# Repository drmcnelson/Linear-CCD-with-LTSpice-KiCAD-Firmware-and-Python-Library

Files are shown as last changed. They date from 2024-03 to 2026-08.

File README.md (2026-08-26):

# Linear-CCD-with-LTSpice-KiCAD-Firmware-and-Python-Library
by Dr M C Nelson (C) 20220-2026 [(the authoritative repo is here)](https://github.com/drmcnelson/Linear-CCD-with-LTSpice-KiCAD-Firmware-and-Python-Library)

<br>

> **Note:** For the **high-linearity version** for quantitative science along with a revised implementation of this all-in-one design but now with hardware locked timing (using the FlexPWM), please see the newer repository: [TCD1304-Sensor-Device-with-Linear-Response-and-16-Bit-Differential-ADC](https://github.com/drmcnelson/TCD1304-Sensor-Device-with-Linear-Response-and-16-Bit-Differential-ADC).

<br>

## Introduction
Linear CCDs can be useful tools in science, for example as a sensor for a spectrometer or imaging system.  And indeed, there are many commercial instruments that are based on low cost linear CCDs such as the Toshiba TC1304 and the Sony IXL511.
Here we provide design files, firmware and software for a device that provides competitive performance and a rich set of science-centric features, and that can be customized to your experiments, all at a fraction of the cost of the commercial offerings.  The design is based on the Toshiba TCD1304 (3648/3694 pixels) and Teensy 4.0 (600MHz ARM, 480MHz USB).  The Teensy 3.2 is plug compatible for this design.
Read further below, and you will find tutorials on electrical design and managing the CCD to provide flexible timing and reproducible measurements so that you can use it as a scientific instrument.

In this repository you will find directories containing (a) electrical design files in KiCad, (b) firmware (a sketch file) for the Teensy, and (c) a Python class library with graphical and command line utilities to operate the device.
The device has a trigger or gate input, sync and busy outputs, and spare pins for digital and analog I/O.
The operating modes include clocked, triggered frames, triggered series of frames, and gated frames (where the shutter is opened and closed on the rising and falling edges of the logic level input signal).
The device appears as a serial port (COM in windows) with comands and response in human language ASCII and frames returned as binary or formatted.
The python class library provides higher level functions, a graphical realtime display and a command line processor.  There is a help command in the firmware and in the Python command line interpreter.  Details of the electrical and firmware design are described later in this README.

The following shows the microcontroller side of the device.  The sensor side can be seen in the image of the spectrometer (below).   The digital I/O pins across the top include trigger input, sync and busy output, pins that monitor the signals going to the sensor, and spares that can be controlled through the user interface.  Across the bottom there are pins that can be used for analog inputs or digital I/O, and 3.3V that can be used for an auxiliary device.

IMG_20231215_144019112_cropped250

Following are two examples of applications; using the sensor in a spectrometer and measurement of spectral-spatial-dynamics in an OLED.  This repository provides what you need in terms of ecad files and software to build one for yourself, or if you like you can contact me for an assembled board.

The files in the repo were produced on a Linux desktop computer (Fedora 37, Cinnamon Spin), using KiCAD 6 for the electrical design and Emacs for the firmware and python programs.

<ul>
 <i>
For next level designs and a preview of our study on linearity and reproducibility in CCDs see our new repo at <a href=https://github.com/drmcnelson/TCD1304-Sensor-Device-with-Linear-Response-and-16-Bit-Differential-ADC>TCD1304 with linear response and 16bit ADC</a>. We suggest perusing both this and the new repo and selecting the implementation that best serves your needs.  Feel free to contact me with questions.
 </i>
</ul>

## Some Example Use Cases

### Spectrometer
The first shows the inside of a spectrometer built with a G1200 grating, two lenses and a slit. The mounts are 3D printed and everything is affixed to a stiff Al plate. There is a cover, not shown here, and specific surfaces are covered with low-reflectance tape.  The spectrum is that of a fluorescent ceiling light through a 200um fiber at a distance of about 8ft, with a 200um slit.

|IMG_20231217_120419719 cropped350|FluorescentLamp Screen500|

### Imaging Spectral-Spatial-Dynamics
The following example uses the sensor device to record the time evolution of the spatial distribution of light produced by an OLED at a current density of 150 $\mu A/cm^2$. The sensor device collects a series of frames wth 10ms shutters at 10ms intervals (back to back), with the series initated on a trigger at the start of the applied voltage waveform. The blue line shows the resulting current density in the OLED, the pale line shows the sync pulses output by the sensor device at the start of each frame, and the red line is the applied voltage (2.41V).  (We plan to post repositories for the DAQ board and current amplifier as well.)

|SampleR1 51 D7_G100K_A2 410v_I0 010s_D0 500s_N005_T4 0C_M17 0000mm_W501 340nm 20230309 080608 827395 tdaq2|SampleR1 51 D7_G100K_A2 410v_I0 010s_D0 500s_N005_T4 0C surface cropped|

# Electrical Design, Analog
The datasheet for the TCD1304 can be found here  https://toshiba.semicon-storage.com/us/semiconductor/product/linear-image-sensors/detail.TCD1304DG.html.
The following table is found on page 4.
We see that $V_{SAT}$ the saturation output volage runs from 450mV to 600mV, $V_{MDK}$ the dark signal is 2mV, thus a dynamic range of 300 (for a 10ms integration integral), $V_{OS}$ the DC output signal is typically 2.5V but can be from 1.5V to 3.5V, and $Z_O$ the output impedance is typically 500 ohms but can be 1K.  So, that is a lot of variation that we need to account for in our design.

TCD1304-optical-electrical

The datasheet provides the following diagram in Note 8 to illustrate the definition of $V_{OS}$.  The hatched area is the negative going output signal.  SS is ground

TCD1304-electrical-note8

For best performance in digitizing the signal, we want a circuit that takes the above signal as input and outputs a signal that matches the input range of our microcontroller's ADC.  The following circuit element shows one approach that does this and can run on a single supply. We can call this a shift, flip and amplify (SFA). The gain is set as usual for an inverting amplifier by $R_2$ and $R_1$ and the potentiometer provides the offset through the + input of the opamp.

SimpleSchematic1

But, recall that the datasheet says the output impedance $Z_0$ varies from 500 ohms to 1k.  If we connect that directly to our SFA then $Z_0$ becomes part of the gain equation, $R1\rightarrow R1+Z_0$, and in a bag of sensors we might find that the gain is different for each sensor.
So, we need to isolate that source impedance from the SFA.

A solution to this is to use an opamp follower as the first stage, as shown in the following crcuit.  The follower presents a very high impedance at its input, which is ideal for reading the voltage from the sensor, and a low impedance at its output, which is ideal as an input to the SFA

TCD1304-opampfollower

Referring again to the datasheet for the TCD1304, we see that (a) we can operate the sensor chip in the range 3V to 5.5V, (b) it requires a clock between 800KHz and 4MHz (2MHz if operated below 4V) and (c) the data readout rate is 1/4 of the clock 200kS/s to 1MS/s (500KS/S if powered below 4V).
Operating with a 3.3V supply, and making efficient use of the full scale range of the ADC,  means that we need to use a rail to rail opamp.
Our SFA architecture means that the opamp has to also have a wide common mode range. 
And the sampling rate means we need to look for a slew at least as faster as 100V/usec

The complete analog front end circuit is shown in the following LTSpice model based on the ADA4807.
We use the first opamp in the package for the voltage follower and the second opamp for the flip, shift,and amplify stage.
Gain and offset are as calculated above.
The green trace is the output from the sensor and the purple curve is the output from the second stage.
As can be seen the 2.5V to 1.9V signal from the sensor becomes a 0.1V to 3.1V for the ADC, and the rise time is small compared to the sampling period.
In our actual circuit we use a trim pot for the voltage applied to V+.

Screenshot from 2023-12-18 08-43-01

It might be noted that we could have chosen a larger gain to look at lower intensity light, or with the Teensy 3.2 we can use its built-in amplifier under software control, provided the offset is small.

## Analog input of the Teensy 4.x and Teensy 3.2
The following diagaram for the analog input, and one similar to this, are found in the datasheets for the i.MXRT106x (Teensy 4) and the K20 (Teensy 3).
This is a modified version of a SAR type analog input.  Normally the input sees the switched sampling capacitor.
Here there is a series resistor in front of the sampling capacitor.

T3analoginput

In operation, the switch closes for a period of time to allow the capacitor to draw charge from the input.
At the end of the sampling period the switch is opened and the voltage on the capacitor is converted to a digital representation in the successive approximation register (SAR).
In other words, precision is determined by the length of the sampling window (in time) versus the RC time constant seen by the sampling capacitor.
Full precision means the voltage on the capacitor is within 1 LSB of the input, at the end of the sampling window.

For a simple RC network, the voltage on the capacitor is $V(t)/V(0) = 1 - exp(-t/RC)$.
Therefore, for n bits of precision, the sampling window needs to be at least $ln(2^{n}) \times RC$.
This works out to be 11 x RC for 16 bits and 8 x RC for 12 bits. 
The following shows this graphically.

samplingtime

For the T3 in 16 bit mode, with RADIN = 2k, and CADIN = 8pf, RC ~ 16nsecs.
The voltage on the sampling capacitor is within $1/2^{16}$ of the input voltage after about 170nsecs.

For the T4 in 12 bit mode, RADIN can be from 5k to 25k and CADIN is 1.5pF, RC ~ 7.5nsecs to 40nsecs.
We need about 60nsecs to 320nsecs to reach 12 bit precision.

Thus the T3 and T4 are both compatible at 500KSPS.  See the [ADC library](https://github.com/pedvide/ADC) for details setting the sampling time and conversion clock.

The tradeoff for the T3 with its 16 bit input, is that the T3 has a much slower USB interface, 1MB/s transfers to the host versus 60MB/s for the T4.
The best frame to frame interval with the T3 is about 16msecs and about 8msecs for the T4.

N.B.  Driving the analog input of an MCU is different from driving a normal SAR type ADC.  Normally, the drive circuit for a SAR includes an external capacitor to serve as a charge reservoir for the sampling capacitor.  This is pre-empted in the MCU analog input by the large internal resistance in series with the sampling capacitor.

## How many bits do I really need?
In the table above, the dynamic range is listed as 300.
This is simply the saturation output voltage 600mv divided by the dark signal 2mV.
If that were the limit, then 10 good bits would be enough.

In principle the dark noise should scale with exposure time or by cooling.  Emperically, using a special low noise linear radiometric design(*), we find that the noise floor for the TCD1304 seems to be at about 0.6mV which it reaches for exposures below about 10msec.  Modest cooling to 4C is reported elsewhere to reduce noise by a factor of 4.  So, we can estimate a practical limit for the dynamic range at about 4,000, or 12 bits.  That is what is offered by the T4 ADC.  If you want to do signal averaging, and given the usual performance specs of ADCs, it is reasonable to have some extra bits, and so a 16 bit ADC is a good choice for a high performance system.

Our analog section uses an ADA4807.  Its datasheet lists the input voltage noise as $3.1 nV/\sqrt Hz$.
At 500KSPS this becomes 2.2uV, and setting the gain at 5, we expect 10uV.  So, we are well ahead of the noise floor for the device.
Without going into a more detailed analysis, we see that our electrical noise can be about 1/2 of the dark signal.
That is workable with some signal averaging.

(*) Our high performance designs with differential signal paths and ADC are posted at
[TCD1304 Sensor Device with Linear Response and 16 bit Differential ADC](https://github.com/drmcnelson/TCD1304-Sensor-Device-with-Linear-Response-and-16-Bit-Differential-ADC)
and
[S11639-01 with 16 bit differentual ADC for SPI](https://github.com/drmcnelson/S11639-01-Linear-CCD-PCB-and-Code).
 Both of these have been built and tested and the repos now have all of the gerbers, bom, firmware and user code.
We plan to upload a repo with a cooled sensor in the near future.   The other advantage of those designs is that they are two board systems and provide better mechanical isolation if your are changing cables after alignment.  But, the design posted here offers sufficient precision and has fewer parts (i.e., it costs less and takes less time to build).

# CCD operation
Operationally, a CCD sensor stores charge in each pixel proportional to light and noise, until assertion of a shift pin causes the contents to be transferred to a buffer and then the contents are shifted along the buffer by a clock to the output pin and appear as a series of voltages.
The TCD1304 has an additional function that controls which shift assertions initiate the readout sequence.
The internal structure is depicted as follows from page 3 of its datasheet.  Externally the device is controlled by three pins, shift SH, integration clear gate ICG, and master clock $\phi M$.

TCD1304-registers

The following two figures from the datasheet show how Toshiba envisions operation of the sensor chip.  As indicated, charge is integrated during the intervals between trailing edges at the SH pin. When the the ICG pin is low the accumulated charges are available in the readout buffer and then shifted to the output pin at a rate of 1 datum per four cycles of the master clock.

TCD1304-timing1

TCD1304-timing2

Toshiba labels the second diagram above as "Electronic Shutter Function".  This refers to the function of ICG in selecting which SH assertion results in charge being available in the readout buffer.  However it is not a shutter in the conventional sense.  It is easily shown experimentally that if the device is left idle, several SH cycles are needed to arrive at a noise level baseline in the readout.   There are a number of commerical CCD systems that clock the SH pin or its equivalent to keep the sensor "clean".  This can have important ramifications if the device is to be triggered, for example for kinetic studies.   Alternatives include good "dark" management, designing the experiment to start with a few blank frames to clear the sensor, and/or having the device initiate the trigger.

Note that it is the low state on the ICG pin that makes the readout available to be clocked out to the OS pin, while the SH pin sets the integration interval.

## Driving the SH, ICG and Master Clock pins
Referring again to the datasheet, page 6, we find the following table.
Notice that the shift gate has a capacitance of 600pF and the integration clear gate has 250pF.
From the magnitude of the capacitances, we might guess that these are closely related to moving charge to the output buffer.



Notice also, that the master clock and data transfer rates are reduced when operating at lower voltages.



The large capacitances also factor into how we drive these pins, rise times with large capacitances are easily current limited.
The preferred way to drive the gate pins is with a buffer and series resistor, as shown in the following.
For a 3.3V drive, a 150 ohm resistor sets the rise to 90nsecs for the SH pin and limits the current to 22mA.
For a 1 usec pulse, this gives a rise time that is less than 1/10 of the pulse width.
The buffer can be a 74LVC1G34, or one channel of a 74VLC3G34, which can drive 25mA.

singlegate

For comparison, the Teensy digital I/O pins provide 4mA.
If the gate is driven directly from the Teensy, the response is current limited, $\Delta t \approx C \Delta V / I$.
That works out to 500nsecs.
So, driving the gates from the digital I/O pins can work, if you can accomodate the longer pulse duration needed for the current limited pulse rise time.

In this repo we provide two sub-directories for designs for the all-in-one TCD1304 and Teensy, with and without the 25mA pulse driver (74VLC3G34).  The verion with 25mA gate drivers is the preferred version.  The KiCad files for that version are [here](TCD1304Rev2GDKiCAD).

For our high-end board with 16 bit ADC and faster timing, see our repo here.

## Frame rates, shutters and timing for data acquisition.
The following diagram from page 9 of the datasheet shows the timing requirements for the ICG and SH pins relative to each other and the master clock.

TCD1304-timingreqs

With a 2MHz master clock, it takes about 7.4ms to read one record from the device into the memory of the microcontroller.  Transfer from the microcontroller to the host PC can take an additional 5ms for the Teensy 3.x (12 Mb/s) or about 120usec with the Teensy 4.x (480 Mb/s).  Needless to say, this sets the maximum frame rate, that is the time between readouts, and is different from the minimum integration interval which depends only on the minimal interval between successive trailing edges at the SH pin.

For data collection, we need to be able to set integration and frame intervals freely (within the physical limits of the sensor) and we need to be able to reliably control timing with respect to an external trigger or gate.   Since the shutter or integration interval is defined by successive assertions of the SH pin, we focus on how these requirements translate to operation of this pin.

The following diagram shows a sequence where the shutter interval is shorter than the inter frame interval, and the frame interval is not necessarily an integer number of shutter intervals in length.  The SH pin operates with alternating short and long intervals.  The frame interval is the sum of these two intervals, or that betwen every second SH.

Shutter-Operation-shortshutter

The following shows back to back shutters with identical frame and shutter intervals.

Shutter-Operation-longshutter

And this one shows a constant shutter interval with the frame interval an integer multiple of the shutter.

Shutter-Operation-modalshutter

Our control logic for operating the device has to accomodate all three scenarios, and we have to be able to initiate frames or sets of frames from a clock or from a trigger.
Architecturally, we set this up as two ISRs, which we call ShutterA_isr() and ShutterB_isr().  The sequences are easily implemented by various combinations of A and B or just B after one A, and easily triggered, gated or clocked as needed.

## Signals, Sync and Busy
The sensor device has a trigger input and two outputs SYNC and BUSY.  Sync can be configured to signal the start of a series of frames or to signal the start of each shutter.  SYNC can also be configured to be followed by a holdoff.  BUSY is set with the start of the first shutter and remains asserted until the last data transfer is complete.   Each pin can be set nominally HIGH or LOW, assertion is the opposite.  Additionally there is a SPARE pin.  Any of the pins can be manually set, cleared, toggled or pulsed.

The following shows the actual operation of the sensor device, green is SH, purple is ICG, blue is SYNC and yellow is BUSY.  We see BUSY goes high immediately, SH and ICG operate as described in the data sheet.  Light is integrated between the two trailing edges and the data is transferred following the second assertion of the SH and clearing of the ICG pins.

Scope-singleframe

## Triggered and gated operation
The following shows a triggered frame.  The commands are "set trigger rising", "trigger 20" to trigger one 20usec frame.  The blue line is the trigger input.  There is a small reproducible delay between the trigger and the shutter, due to certain fixed timings involved in getting the shutter started.  Notice the alignment of the BUSY and SH signals.

Scope-triggerd

The following shows a gated frame, blue is the gate signal.  The commands are "set trigger change", "gate 1", to gate one frame.  For this, the spare pin is connected to the trigger input and we enter the command "pulse spare 20" to output a 20 usec pulse.  As you can see the shutter sequence begins and finishes with the gate.

Scope-gated

# Data processing
Referring to the clock diagrams above, we see that the data record comprises 12 dummy outputs followed by 13 light shielded elements, followed by 3 shadowed elements, followed by the 3648 elements making up the effective output and followed by another 14 dummy elements.   Thus elements 12 thru 24 provide a baseline which we can average or take the median and subtract from elements 28 through 2675 which form the image.   In the spirit of "always preserve primary data", we do not do this substraction nor any scaling, in firmware.  Rather we pass the entire record as is, to the PC host and the host software is responsible for subtracting and scaling as appropriate.

# Firwmare
The firmware subdirectory contains a sketch for Teensy 4.0.  After assembling your board (or obtaining one from the author), you can mount your Teensy 4 and TCD1304 detector, and then flash the program into the Teensy 4.0.   The commands are in english, ASCII over USB.  Enter the command "help" to get a listing and short explanation of the commands.  A listing of the help text is included in the Python subdirectory.

The default action returns the data in binary.  You will ideally want to use a multi-threaded program on your host computor, with one thead reading the responses and data and queuing as appropriate to a separate graphics thread.   The Python code provides a Class for the device that handles all of this.

# Python
The Python subdirectory contains a file TCD1304Rev2Controller.py and three library files that it looks for in its directory.  The program implements threads using the multitasking interface in Linux.  A dedicated thread reads the responses from the device and queues data to an internal data queue for the "save" command and to a queue read by the runtime graphics thread.  The Python program has a help command, like the firmware.

# Adjusting the offset
With a voltmeter or scope, the middle pin on the trim pot should be set close to 2.1 volts.  Then in the Python program, issue the commands "baseline off" and "clock 1000 10000 100000".   This wil turn off the baseline subtraction function and clock 1000 frames with an integration time of 10ms spaced at intervals of 100ms.   Try the commands "stop", "baseline on" and repeat the clock command to see a comparison.  You can zoom in on the graphical display and use a small screwdriver to adjust the offset.   I usually put the sensor in a drawer or cover it with a black cloth while I do this.

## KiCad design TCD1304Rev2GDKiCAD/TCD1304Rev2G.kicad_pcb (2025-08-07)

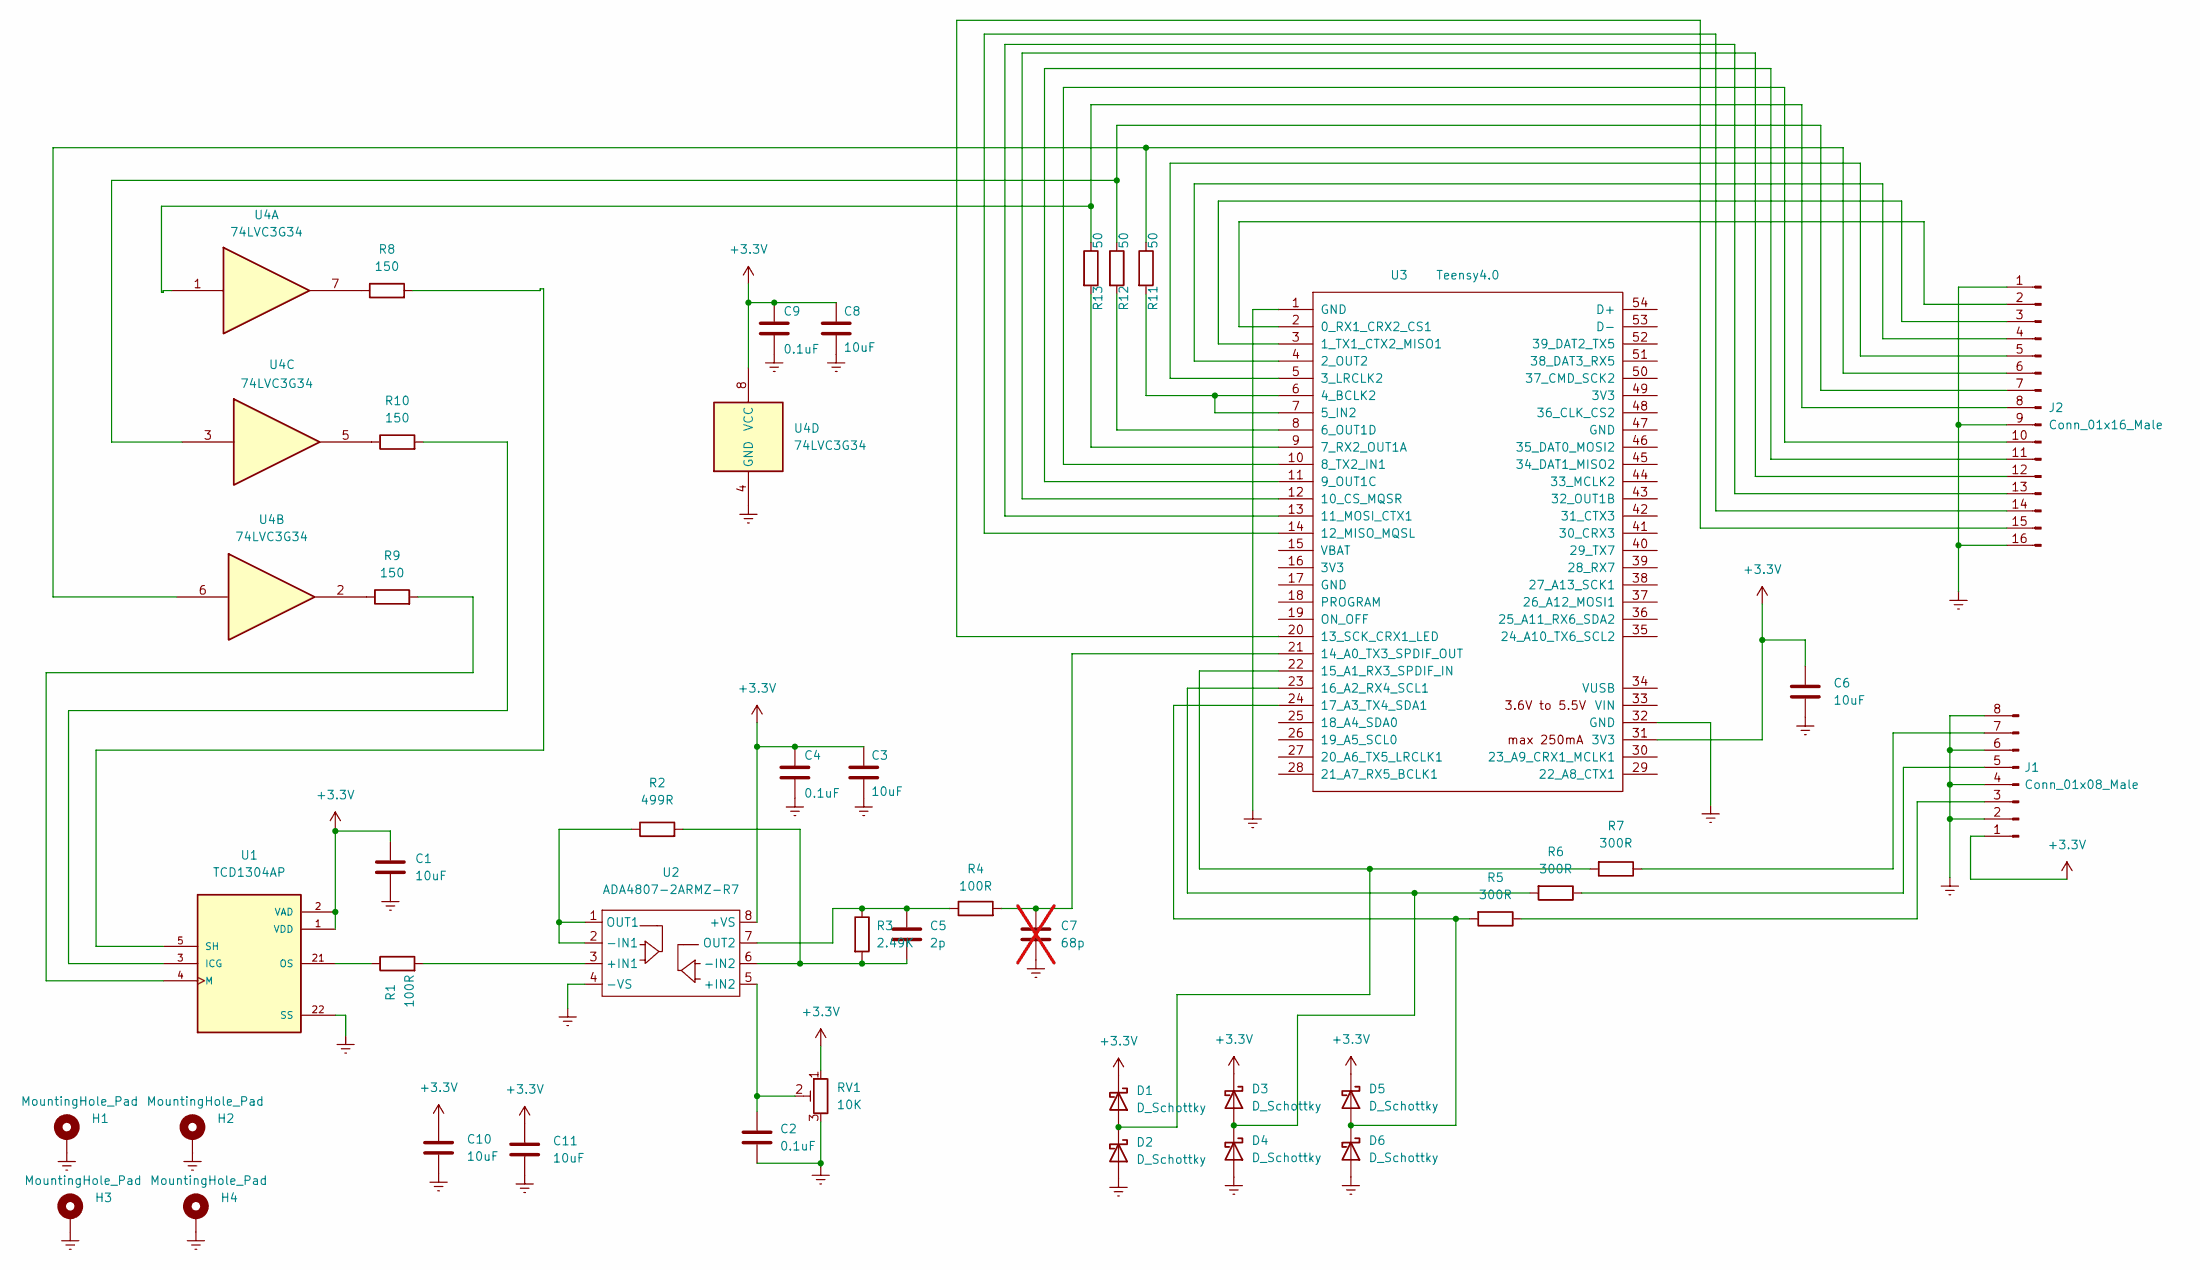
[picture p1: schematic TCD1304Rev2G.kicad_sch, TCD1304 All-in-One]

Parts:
C1, C3, C6, C8, C10, C11: 10uF; C_0603_1608Metric; Digikey 490-12317-1-ND
C2, C4, C9: 0.1uF; C_0603_1608Metric; Digikey 399-C0603X104J3RACAUTOCT-ND
C5: 2p; C_0603_1608Metric; Digikey 1284-1196-1-ND
C7: 68p; C_0603_1608Metric; Digikey 1276-1135-1-ND; not fitted
D1, D2, D3, D4, D5, D6: D_Schottky; D_SOD-323; Digikey CUS520H3FCT-ND
H1, H2, H3, H4: MountingHole_Pad; MountingHole_3.2mm_M3_DIN965_Pad
J1: Conn_01x08_Male; PinHeader_1x08_P2.54mm_Vertical; Digikey 3M156268-08-ND
J2: Conn_01x16_Male; PinHeader_1x16_P2.54mm_Vertical; Digikey 3M156268-16-ND
R1, R4: 100R; R_0603_1608Metric; Digikey 2019-RK73H1JTTD1000FCT-ND
R2: 499R; R_0603_1608Metric; Digikey 2019-RK73H1JTTD4990FCT-ND
R3: 2.49K; R_0603_1608Metric; Digikey 311-2.49KHRCT-ND
R5, R6, R7: 300R; R_0603_1608Metric; Digikey 2019-RK73H1JTTD3000FCT-ND
R8, R9, R10: 150; R_0603_1608Metric_Pad0.98x0.95mm_HandSolder; Digikey A130406CT-ND
R11, R12, R13: 50; R_0603_1608Metric_Pad0.98x0.95mm_HandSolder; Digikey 541-2784-1-ND
RV1: 10K; TRIM_3296W-1-502LF; Digikey 3296W-103LF-ND
U1: TCD1304AP; DIP1016W47P254L4210H372Q22; Digikey 110-87-422-41-001101
U2: ADA4807-2ARMZ-R7; MSOP-8_3x3mm_P0.65mm; Digikey ADA4807-2ARMZ-R7CT-ND
U3: Teensy4.0; Teensy40; Digikey 1568-DEV-16997-ND
U4: 74LVC3G34; TSSOP-8_3x3mm_P0.65mm; Digikey 1727-6685-1-ND

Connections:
+3.3V: C1.1, C3.1, C4.1, C6.1, C8.1, C9.1, C10.1, C11.1, D1.1 (K), D3.1 (K), D5.1 (K), J1.1, RV1.1, U1.1 (VDD), U1.2 (VAD), U2.8 (+VS), U3.31 (3V3), U4.8 (VCC)
Earth: C1.2, C2.2, C3.2, C4.2, C6.2, C7.2, C8.2, C9.2, C10.2, C11.2, D2.2 (A), D4.2 (A), D6.2 (A), H1.1, H2.1, H3.1, H4.1, J1.2, J1.4, J1.6, J1.8, J2.1, J2.9, J2.16, RV1.3, U1.22 (SS), U2.4 (-VS), U3.1 (GND), U3.32 (GND), U4.4 (GND)
unnamed: D1.2 (A), D2.1 (K), R7.2, U3.22 (15_A1_RX3_SPDIF_IN)
unnamed: D3.2 (A), D4.1 (K), R6.2, U3.23 (16_A2_RX4_SCL1)
unnamed: D5.2 (A), D6.1 (K), R5.2, U3.24 (17_A3_TX4_SDA1)
unnamed: J1.3, R5.1
unnamed: J1.5, R6.1
unnamed: J1.7, R7.1
unnamed: J2.2, U3.2 (0_RX1_CRX2_CS1)
unnamed: J2.3, U3.3 (1_TX1_CTX2_MISO1)
unnamed: J2.4, U3.4 (2_OUT2)
unnamed: J2.5, U3.5 (3_LRCLK2)
unnamed: J2.6, R11.1, U4.6
unnamed: J2.7, R12.1, U4.3
unnamed: J2.8, R13.1, U4.1
unnamed: J2.10, U3.10 (8_TX2_IN1)
unnamed: J2.11, U3.11 (9_OUT1C)
unnamed: J2.12, U3.12 (10_CS_MQSR)
unnamed: J2.13, U3.13 (11_MOSI_CTX1)
unnamed: J2.14, U3.14 (12_MISO_MQSL)
unnamed: J2.15, U3.20 (13_SCK_CRX1_LED)
unnamed: R8.1, U4.7
unnamed: R9.1, U4.2
unnamed: R10.1, U4.5
unnamed: R10.2, U1.3 (ICG)
unnamed: R9.2, U1.4 (M)
unnamed: R1.1, U1.21 (OS)
unnamed: R8.2, U1.5 (SH)
unnamed: R1.2, U2.3 (+IN1)
unnamed: C2.1, RV1.2, U2.5 (+IN2)
unnamed: R2.1, U2.1 (OUT1), U2.2 (-IN1)
unnamed: C5.2, R2.2, R3.2, U2.6 (-IN2)
unnamed: C5.1, R3.1, R4.1, U2.7 (OUT2)
unnamed: R11.2, U3.6 (4_BCLK2), U3.7 (5_IN2)
unnamed: R12.2, U3.8 (6_OUT1D)
unnamed: R13.2, U3.9 (7_RX2_OUT1A)
unnamed: C7.1, R4.2, U3.21 (14_A0_TX3_SPDIF_OUT)

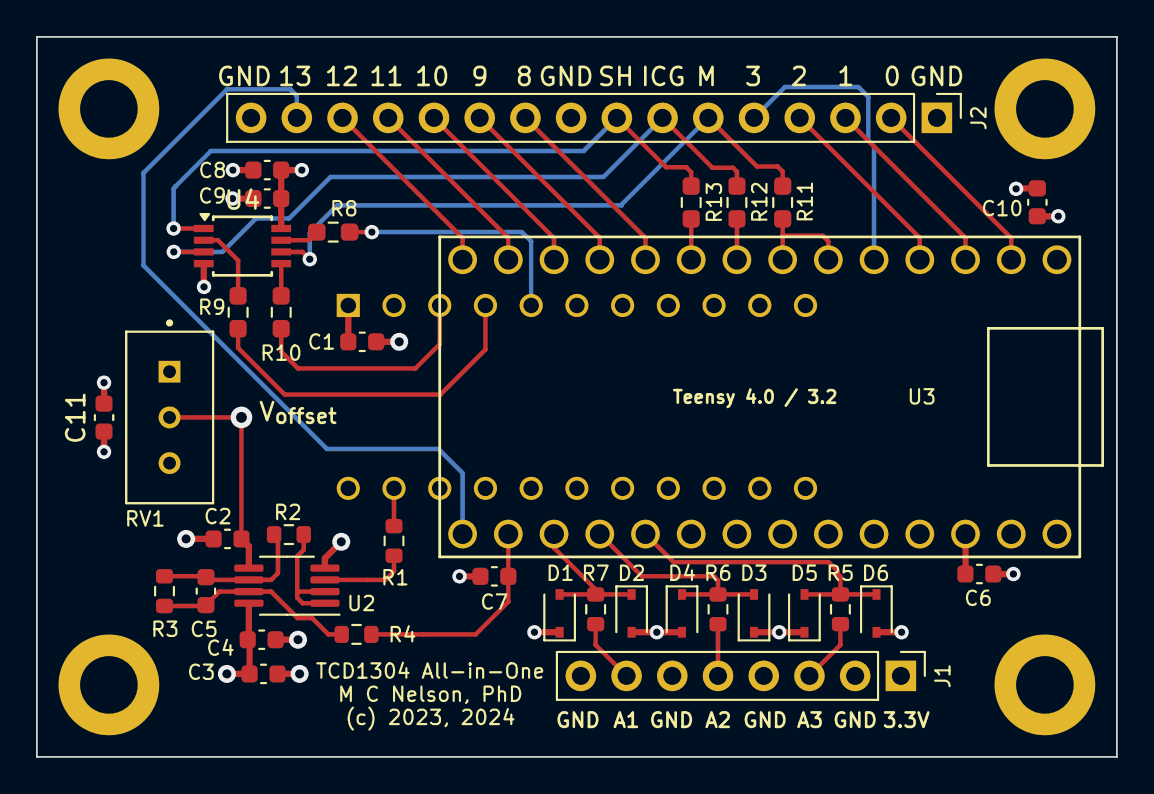
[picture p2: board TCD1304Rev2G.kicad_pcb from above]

Board: 4 copper layers, 60.0 x 40.0 mm, 41 parts (1 on the bottom side), 37 nets.

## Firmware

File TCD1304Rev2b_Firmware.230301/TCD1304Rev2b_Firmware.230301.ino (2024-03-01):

/*
  Author:   Mitchell C. Nelson
  Date:     March 1, 2024
  Contact:  drmcnelson@gmail.com

  TCD1304 rev 2 only.   This version removes support for ILX11 and earlier versions of the TCD1304
  
  This work is a derivative of the following works:
  
    RAWHIDfirmware.ino   Mitchell C. Nelson,  June 18, 2021

    TCD1304_201223.ino   Mitchell C. Nelson,  Aug 10 through Dec 23, 2020


  Permissions:

     Permission is hereby granted for non-commercial use.

     For commerical uses, please contact the author at the above email address.

  Provisos:

  1) No representation is offered or assumed of suitability for any purposee whatsoever.

  2) Use entirely at your own risk.

  3) Please cite appropriately in any work using this code.

 */

// ------------------------------------------------------------------
#define DIAGNOSTICS
//#define DIAGNOSTICS_CPU
//#define DIAGNOSTICS_IDLER
//#define DIAGNOSTICS_SYNC
//#define DIAGNOSTICS_GATE
// Stream& dataPort = SerialUSB1;
// ------------------------------------------------------------------

#include "Arduino.h"

//#include <digitalWriteFast.h>

#include <limits.h>

#include <ADC.h>
#include <ADC_util.h>

#include <EEPROM.h>

#include <LittleFS.h>

LittleFS_Program filesys;
bool filesys_ready = false;

extern float tempmonGetTemp(void);

// ADC setup
ADC *adc = new ADC();

// CPU Cycles per Usec
#define CYCLES_PER_USEC (F_CPU / 1000000)

// ------------------------------------------------------------------

#define thisMANUFACTURER_NAME {'D','R','M','C','N','E','L','S','O','N' }
#define thisMANUFACTURER_NAME_LEN 10

#define thisPRODUCT_NAME {'T','C','D','1','3','0','4','V','2','B'}
#define thisPRODUCT_NAME_LEN 10

#define thisPRODUCT_SERIAL_NUMBER { 'S','N','0','0','0','0','0','0','0','0','0','1' }
#define thisPRODUCT_SERIAL_NUMBER_LEN 12

extern "C"
{
  struct usb_string_descriptor_struct_manufacturer
  {
    uint8_t bLength;
    uint8_t bDescriptorType;
    uint16_t wString[thisMANUFACTURER_NAME_LEN];
  };

  usb_string_descriptor_struct_manufacturer usb_string_manufacturer_name = {
    2 + thisMANUFACTURER_NAME_LEN * 2,
    3,
    thisMANUFACTURER_NAME
  };

  // -------------------------------------------------
  
  struct usb_string_descriptor_struct_product
  {
    uint8_t bLength;
    uint8_t bDescriptorType;
    uint16_t wString[thisPRODUCT_NAME_LEN];
  };

  usb_string_descriptor_struct_product usb_string_product_name = {
    2 + thisPRODUCT_NAME_LEN * 2,
    3,
    thisPRODUCT_NAME
  };

  // -------------------------------------------------
  
  struct usb_string_descriptor_struct_serial_number
  {
    uint8_t bLength;
    uint8_t bDescriptorType;
    uint16_t wString[thisPRODUCT_SERIAL_NUMBER_LEN];
  };

  usb_string_descriptor_struct_serial_number usb_string_serial_number =
    {
      2 + thisPRODUCT_SERIAL_NUMBER_LEN * 2, 
      3,
      thisPRODUCT_SERIAL_NUMBER
    };
}

// ------------------------------------------------------------------

const char versionstr[] = "T4LCD vers 0.3";

const char authorstr[] =  "(c) 2020-2024 by Mitchell C. Nelson, Ph.D. ";

const char sensorstr[] = "TCD1304";

// ------------------------------------------------------------------

const unsigned long fM  = 2000000;   // 2MHz Mclk frequency

const int syncPin      = 0;     // Goes low for trigger standoff (delay) period, use this for desktop N2 laser
const int busyPin      = 1;     // Gate output pin, goes high during shutter
const int interruptPin = 2;     // Trigger input pin
const int sparePin     = 3;     // Spare pin for digital output
const int fMPin        = 4;     // Mclk out 
const int fMPinMonitor = 5;     // Clock monitor
const int ICGPin       = 6;     // Integration clear gate
const int SHPin        = 7;     // Shift gate
const int analogPin    = A0;    // Analog input, Pin 14

// Fast nofrills CLOCK read
#define CLOCKREAD (CORE_PIN5_PINREG & CORE_PIN5_BITMASK)

// Fast nofrills BUSY pin set, lear, flip state
#define SETBUSYPIN (CORE_PIN1_PORTSET = CORE_PIN1_BITMASK)
#define CLEARBUSYPIN (CORE_PIN1_PORTCLEAR = CORE_PIN1_BITMASK)
#define TOGGLEBUSYPIN (CORE_PIN1_PORTTOGGLE = CORE_PIN1_BITMASK)

// Fast nofrills SYNC pin set/clear
#define SETSYNCPIN (CORE_PIN0_PORTSET = CORE_PIN0_BITMASK)
#define CLEARSYNCPIN (CORE_PIN0_PORTCLEAR = CORE_PIN0_BITMASK)
#define TOGGLESYNCPIN (CORE_PIN0_PORTTOGGLE = CORE_PIN0_BITMASK)

// Conversion to volts
#define NBITS 12
#define VFS (3.3/4.0)
#define VPERBIT (VFS/(1<<NBITS))

// Sensor data readout
#define NREADOUT 3694
#define DATASTART 12
#define DATASTOP 3680

// Size of the useful part
#define NPIXELS (DATASTOP-DATASTART)
#define NBYTES (NPIXELS*2)

// And first part of that is dark
#define NDARK 13

// Transfer time for uint16's over usb 
#define TRANSFERUSECS 7500

// Minimum inter shutter interval
#define SHUTTERMIN 5 

// Pin 13 for the LED
#define HASLED
const int led = 13;

void blink() {
  digitalWrite(led, HIGH);   // turn the LED on (HIGH is the voltage level)
  delay(100);               // wait for a second
  digitalWrite(led, LOW);    // turn the LED off by making the voltage LOW
}

/* =====================================================================================================
   Some pin functions and defaults
*/
int intedgemode = RISING;        // Default trigger mode

// busy pin
unsigned int busyPinState = LOW;

// sync pin
unsigned int syncPinState = HIGH;

// Spare pin can double as PWM
unsigned int sparePinState = LOW;
bool spare_pwm = false;

uint32_t pwm_resolution = 8;
uint32_t pwm_value = 4;
float pwm_frequency = 0.;

void sparePWM_stop() {
  pinMode(sparePin,OUTPUT);
  digitalWriteFast(sparePin, sparePinState);
  spare_pwm = false;
}

void sparePWM_start() {

  float f;
  
  f = F_CPU/(1<<pwm_resolution);
  f /= 4;

  pwm_frequency = f;

  Serial.print( "PWM resolution " );
  Serial.println( pwm_resolution );
  analogWriteResolution(pwm_resolution);  // only for the next call
	
  Serial.print( "PWM Frequency " );
  Serial.println( f );
  analogWriteFrequency(sparePin, f);


  Serial.print( "PWM value " );
  Serial.println( pwm_value );
  analogWrite(sparePin,pwm_value);
	
  spare_pwm = true;
}

void pulsePin( unsigned int pin, unsigned int usecs ) {
  digitalToggleFast(pin);
  delayMicroseconds(usecs);
  digitalToggleFast(pin);
}

/* --------------------------------------------------------
   Extension of the interrupt API, re-enable pin interrupt after dropping pending
 */
#define IMR_INDEX   5
#define ISR_INDEX   6

void resumePinInterrupts(uint8_t pin)
{
	if (pin >= CORE_NUM_DIGITAL) return;
	volatile uint32_t *gpio = portOutputRegister(pin);
	uint32_t mask = digitalPinToBitMask(pin);
        gpio[ISR_INDEX] = mask;  // clear pending
	gpio[IMR_INDEX] |= mask;  // re-enable
}

void disablePinInterrupts(uint8_t pin)
{
	if (pin >= CORE_NUM_DIGITAL) return;
	volatile uint32_t *gpio = portOutputRegister(pin);
	uint32_t mask = digitalPinToBitMask(pin);
	gpio[IMR_INDEX] &= ~mask;
}

/* ===================================================================================================
   Timer functions
*/
elapsedMicros elapsed_usecs;

elapsedMicros diagnostic_usecs;
bool diagnostics = false;

uint64_t cycles64( )
{
  static uint32_t oldCycles = ARM_DWT_CYCCNT;
  static uint32_t highDWORD = 0;

  uint32_t newCycles = ARM_DWT_CYCCNT;

  if (newCycles < oldCycles) {
    ++highDWORD;
  }
  oldCycles = newCycles;
  
  return (((uint64_t)highDWORD << 32) | newCycles);
}

/* ===================================================================================================
   External USB command buffer
*/
#define RCVLEN 256
char rcvbuffer[RCVLEN];
uint16_t nrcvbuf = 0;

#define SNDLEN 256
char sndbuffer[SNDLEN];

/* --------------------------------------------------------
   Raw data and send buffers
*/
#define NBUFFERS 16
uint16_t buffers[NBUFFERS][NREADOUT] = { { 0 } };
uint16_t buffer_index = 0;
uint16_t *bufferp = &buffers[buffer_index][0];

/* Data transfer format
 */
#define BINARY 0
#define ASCII 1
unsigned int dataformat = BINARY;
unsigned int counter = 0;

/* --------------------------------------------------------
   For signal averaging, c.f. for dark spectra
   (not implemented yet, ISR and command interface)
 */
uint32_t accumulator[NREADOUT] = { 0  };
uint accumulatorCounter = 0;
bool do_accumulation = false;

/* --------------------------------------------------------
   Data buffer selector functions
 */

inline void initbufferselect( ) {
  buffer_index = 0;
  bufferp = &buffers[0][0];
}

void selectbuffer( unsigned int iselect ) {
  buffer_index = iselect % NBUFFERS;
  bufferp = &buffers[buffer_index][0];
}

void incrementbuffer( ) {
  buffer_index = ( buffer_index + 1 ) % NBUFFERS;
  bufferp = &buffers[buffer_index][0];
}

/* =====================================================================================
   Built-in ADC readout
*/
inline int fastAnalogRead( uint8_t pin ) {
  adc->adc0->startReadFast(pin);
  while ( adc->adc0->isConverting() );
  return adc->adc0->readSingle();
}

unsigned int measureADCspeed( uint8_t pin, unsigned int knt ) {
  
  uint16_t *p16 = bufferp;
  
  unsigned int usecs;

  Serial.print( "test adc " );
  Serial.println( knt );

  elapsed_usecs = 0;

  for ( unsigned int m = 0; m < knt ; m++ ) {
    for ( int n = 0; n < NREADOUT; n++ ) {
      *p16++ = fastAnalogRead(pin);
    }
    p16 = bufferp;
  }

  usecs = elapsed_usecs;

  Serial.print( "elapsed usecs " );
  Serial.println( usecs );
  
  return usecs;
}

/* --------------------------------------------------------
   ADC single reads
   (note that the alpha0 board used the first two channels)
 */
#define NADC_CHANNELS 4
#define ADC_RESOLUTION (3.3/4096.)
uint16_t adc_data[NADC_CHANNELS] = { 0 };

// Set this to something more than 0 to turn on adc reporting.
unsigned int adc_averages = 0;

/* Send ADC readings
 */
void sendADCs( unsigned int averages ) {

  unsigned int i;
  float scalefactor = ADC_RESOLUTION/averages;
  float val;

  int n = averages;

  for( i = 0 ; i < NADC_CHANNELS; i++ ) {
    adc_data[i] = fastAnalogRead( i );
  }
  n--;
  
  while( n-- ) {
    for( i = 0 ; i < NADC_CHANNELS; i++ ) {
      adc_data[i] += fastAnalogRead( i );
    }
  }
  
  Serial.print( "ADCAVGS " );
  Serial.println( averages );
  
  Serial.print( "ADCDATA" );
  for( i = 0 ; i < NADC_CHANNELS; i++ ) {
    val = adc_data[i] * scalefactor;
    Serial.print( " " );
    Serial.print( val, 5 );
  }
  
  Serial.println( "" );
}

/* --------------------------------------------------------
   Send chip temperature
 */

// Set this to something more than 0 to turn on chip temperature reporting
unsigned int chipTemp_averages = 0;

void sendChipTemperature( unsigned int averages ){
  Serial.print( "CHIPTEMPERATURE " );
  Serial.println( tempmonGetTemp() );
}

/* ===========================================================================================
 * EEPROM support for saving identifier and coordinate mapping constants
 */
#define EEPROM_SIZE 1080

#define EEPROM_ID_ADDR 0
#define EEPROM_ID_LEN 64

#define EEPROM_COEFF_ADDR 64
#define EEPROM_NCOEFFS 4
#define EEPROM_COEFF_LEN ( EEPROM_NCOEFFS * sizeof( float) )

#define EEPROM_RESP_ADDR (EEPROM_COEFF_ADDR + EEPROM_COEFF_LEN)
#define EEPROM_NRESPS 4
#define EEPROM_RESP_LEN ( EEPROM_NRESPS * sizeof( float) )

#define EEPROM_UNITS_ADDR ( EEPROM_RESP_ADDR + EEPROM_RESP_LEN )
#define EEPROM_NUNITS 8
#define EEPROM_UNITS_LEN EEPROM_NUNITS

void eeread( unsigned int address, int nbytes, char *p ) {
  while( nbytes-- > 0  && address < EEPROM_SIZE ) {
    *p++ = EEPROM.read(address++);
  }
}

void eewrite( unsigned int address, int nbytes, char *p ) {
  while( nbytes-- > 0 && address < EEPROM_SIZE ) {
    EEPROM.write(address++, *p++);
  }
}

// -------------------------------------------------------------

void eereadUntil( unsigned int address, int nbytes, char *p ) {
  char b = 0xFF;
  while( nbytes-- > 0  && address < EEPROM_SIZE && b ) {
    b = EEPROM.read(address++);
    *p++ = b;
  }
}
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

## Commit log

2023-12-18 KiCAD files for TCD1304 Rev2
    These are the KiCAD project, schematic and pcb files.
    [TCD1304Rev2.kicad_pcb, TCD1304Rev2.kicad_sch]
2023-12-18 LTSpice file for the sensor and front end circuit
    LTSpice model for the sensor and front end circuit.
2023-12-18 TCD1304Rev2 KiCAD files
    [TCD1304Rev2.kicad_pcb, TCD1304Rev2.kicad_sch]
2024-02-07 Update TCD1304Rev2b_Firmware.231218.ino
    Add to the comment for the clock monitor pin
2024-12-24 Correction
    C7 should be 68p and DNP (do not populate). Normally, for a SAR type input, best results are obtain with an external resistor and capacitor to act as a charge reservoir for the sampling capacitor. Bu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
    [TCD1304Rev2.kicad_pcb]
2024-12-24 Expand explanation of the front end circuit
2024-12-24 All-in-One TCD1304 update, with gate drivers
    This version uses a 74LVC3G34 to drive the SH, ICG and master clock pins.
    [TCD13042c.kicad_pcb, TCD13042c.kicad_sch, TCD13042c_BOM.xls]
2024-12-24 Discusses analog inputs, when to use 16 bits and upcoming cooled sensors
2024-12-26 Minor changes (best practice update)
    [TCD1304Rev2.kicad_pcb, TCD1304Rev2.kicad_sch]
2025-08-07 Correct footprint for U4 (74LVC3G34)
    With apologies, this update corrects the footprint for the 74LVC3G34, to match that for the part listed in the schematic BOM, the NXP 74LVC3G34DP,125, Digikey part number 1727-6685-1-ND.
    The KiCAD footprint library contains two versions of TSSOP-8, size 4.4mm and 3.3m. This part matches the smaller TSSOP-8.
    [TCD1304_All-in-One.kicad_pcb, TCD1304_All-in-One.kicad_sch]
2025-08-19 Delete TCD1304Rev2c_KiCAD directory
    this version in testing, to be restored later
    [TCD13042c.kicad_pcb, TCD13042c.kicad_sch, TCD13042c_BOM.xls, TCD1304_All-in-One.kicad_pcb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]
2025-08-19 Update README.md
    Update for noise measurements and current designs
2025-11-10 All In One TCD1304 with buffer gate driver
    [TCD1304Rev2G.kicad_pcb, TCD1304Rev2G.kicad_sch]

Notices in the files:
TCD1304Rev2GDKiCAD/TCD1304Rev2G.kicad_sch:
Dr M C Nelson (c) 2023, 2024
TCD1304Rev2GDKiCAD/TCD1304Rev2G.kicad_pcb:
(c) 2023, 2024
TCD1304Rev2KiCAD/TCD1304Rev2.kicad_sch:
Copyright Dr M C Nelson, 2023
